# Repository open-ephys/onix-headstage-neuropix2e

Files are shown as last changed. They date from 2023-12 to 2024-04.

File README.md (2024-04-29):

# ONIX Neuropixels 2.0 Headstage

Serialized, multifunction ONIX headstage for IMEC Neuropixels-2.0 probes

**Features**
- 2x [Neuropixels 2.0](https://www.neuropixels.org/) probes per headstage
- Integrated absolute orientation tracking
- Single, 0.3 mm diameter micro-coaxial tether
- Torque-free commutation when used with an [ONIX Commutator](https://github.com/open-ephys/onix-commutator)
- 0.64 grams

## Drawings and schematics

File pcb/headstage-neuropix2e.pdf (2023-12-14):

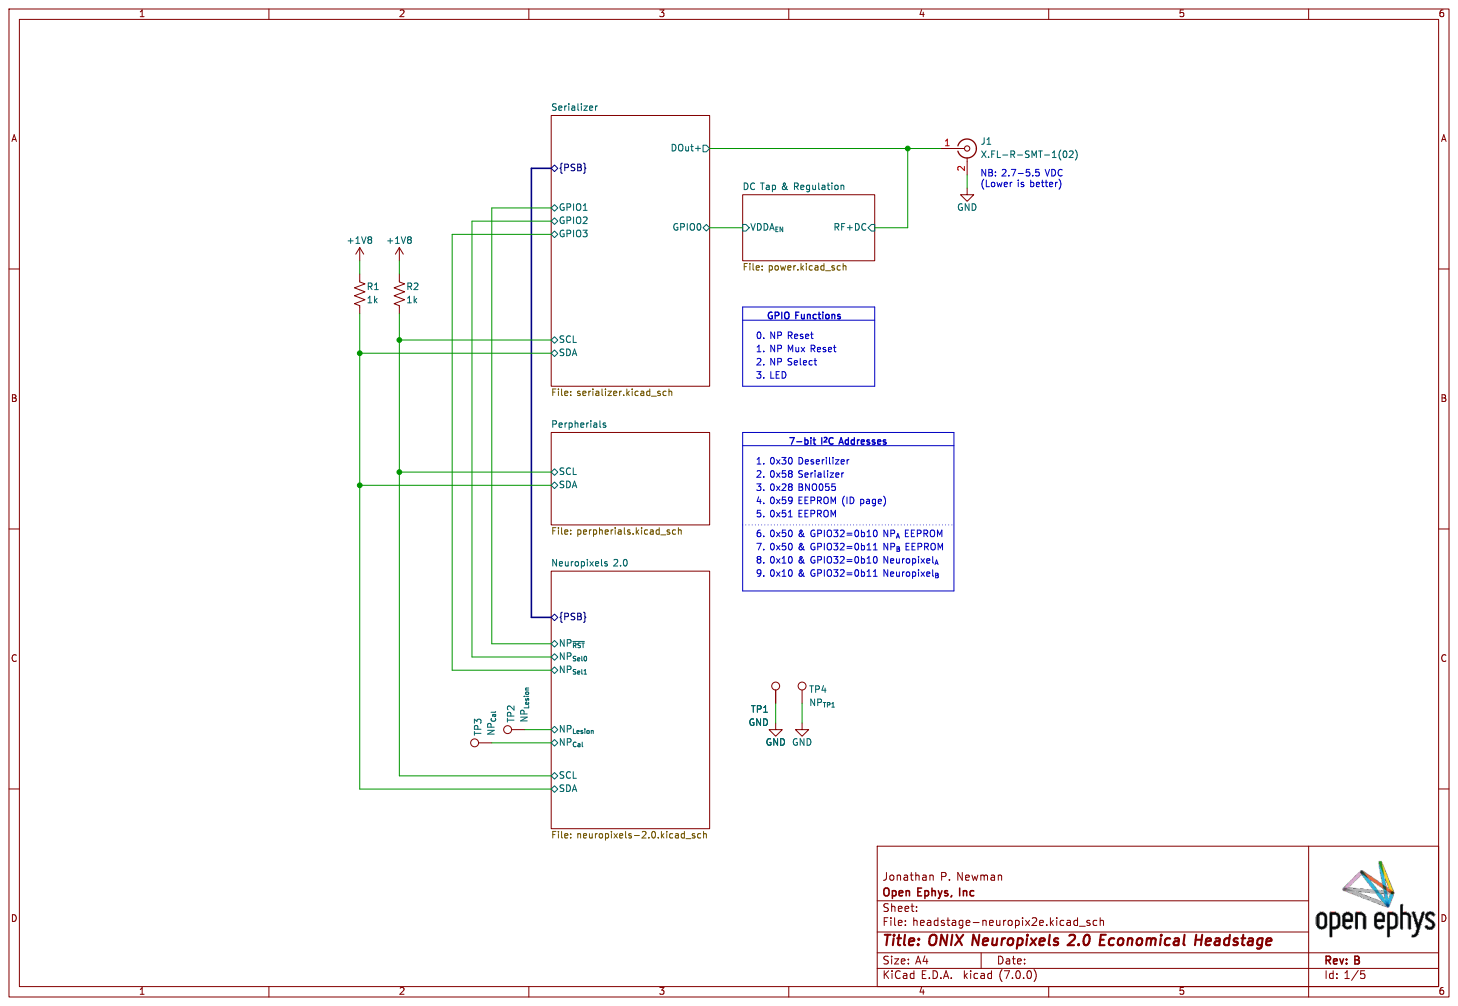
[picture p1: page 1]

{PSB} GPIO3 Serializer File: serializer.kicad_sch SDA

2. NP Select 0. NP Reset 2. 0x58 Serializer GND

1. 0x30 Deserilizer 1. NP Mux Reset GPIO Functions

Id: 1/5 Title: ONIX Neuropixels 2.0 Economical Headstage

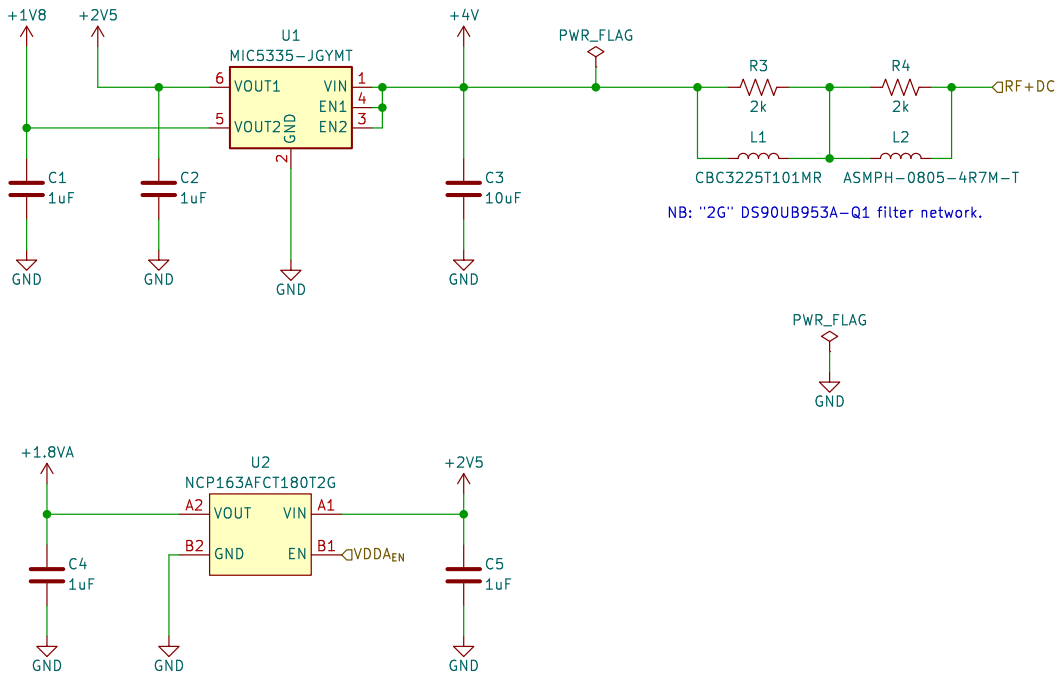
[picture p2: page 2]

Id: 5/5 Title: ONIX Neuropixels 2.0 Economical Headstage

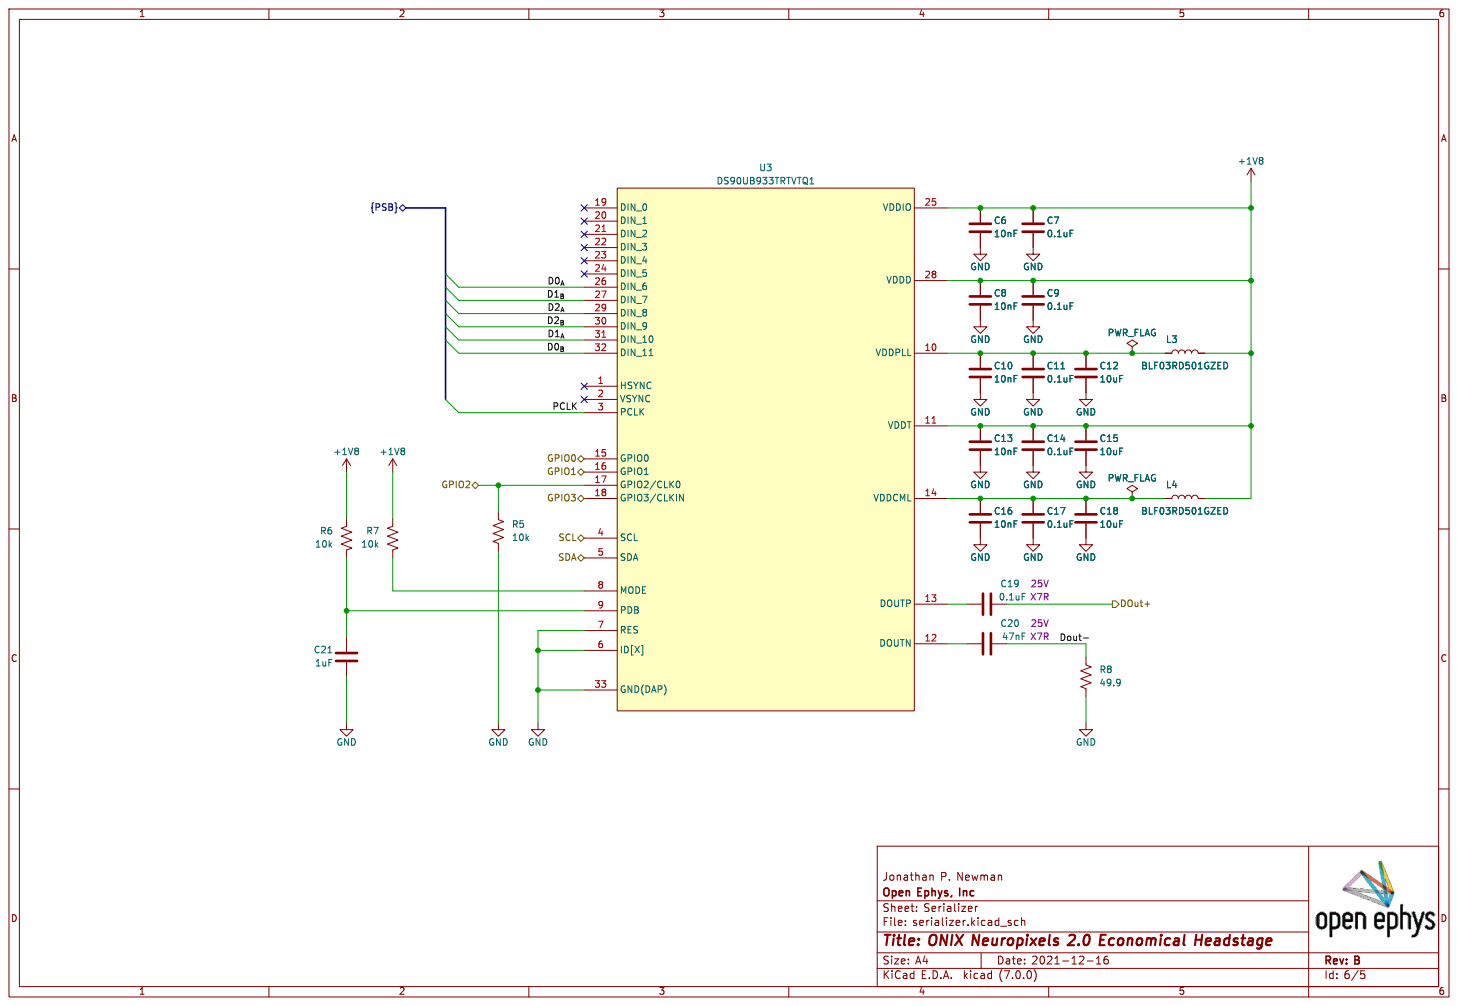
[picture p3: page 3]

Id: 6/5 Title: ONIX Neuropixels 2.0 Economical Headstage

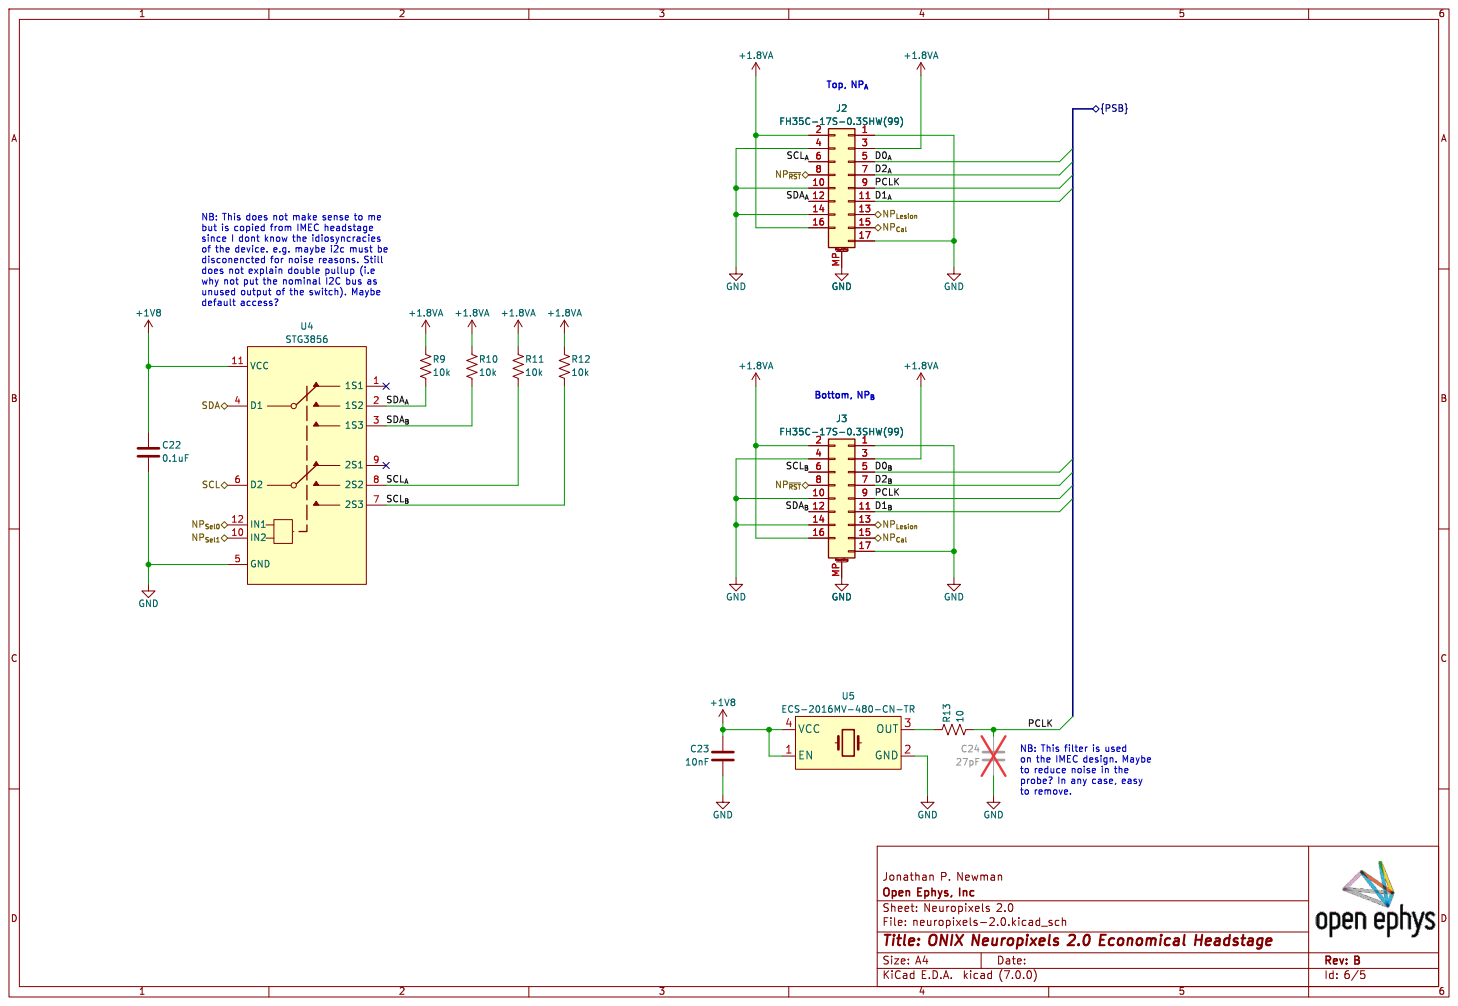
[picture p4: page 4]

Top, NP_{A} NB: This does not make sense to me

but is copied from IMEC headstage
since I dont know the idiosyncracies of the device. e.g. maybe i2c must be

why not put the nominal I2C bus as unused output of the switch). Maybe

on the IMEC design. Maybe
to reduce noise in the
probe? In any case, easy

Id: 6/5 Title: ONIX Neuropixels 2.0 Economical Headstage

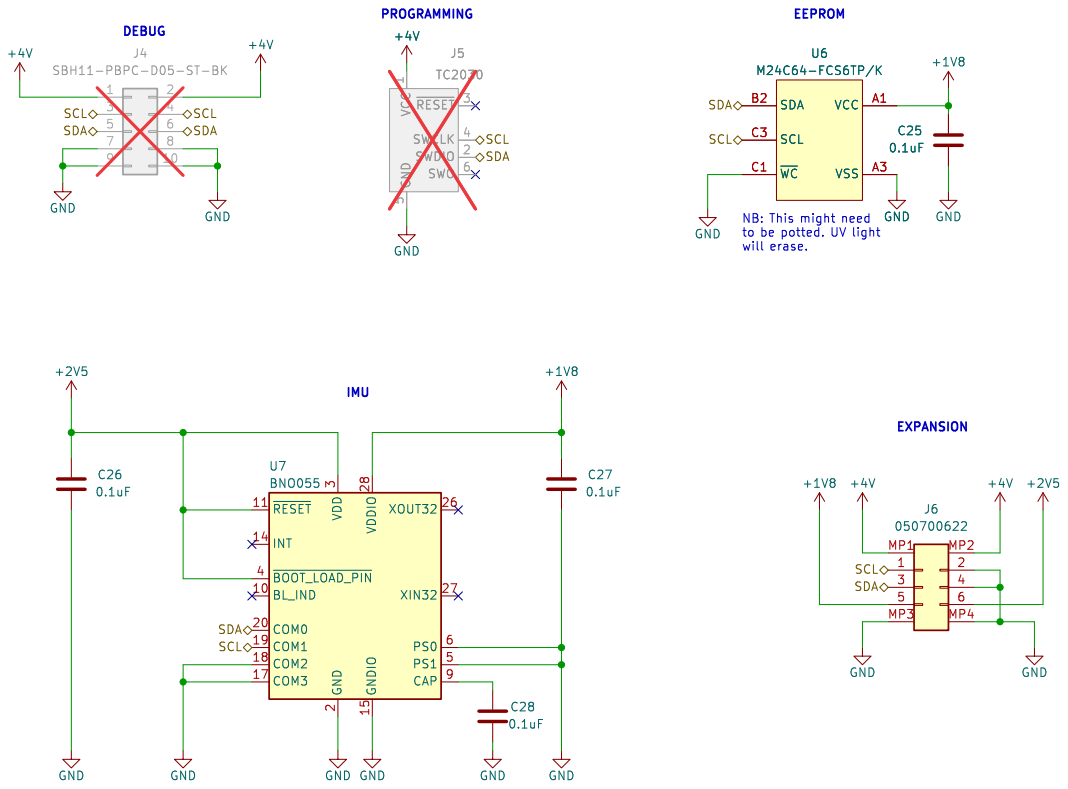
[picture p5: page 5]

1 SWDIO 2 ~{RESET}3 SWCLK 4 GND

NB: This might need
to be potted. UV light will erase.

File: perpherials.kicad_sch Sheet: Perpherials
Id: 7/5 Title: ONIX Neuropixels 2.0 Economical Headstage

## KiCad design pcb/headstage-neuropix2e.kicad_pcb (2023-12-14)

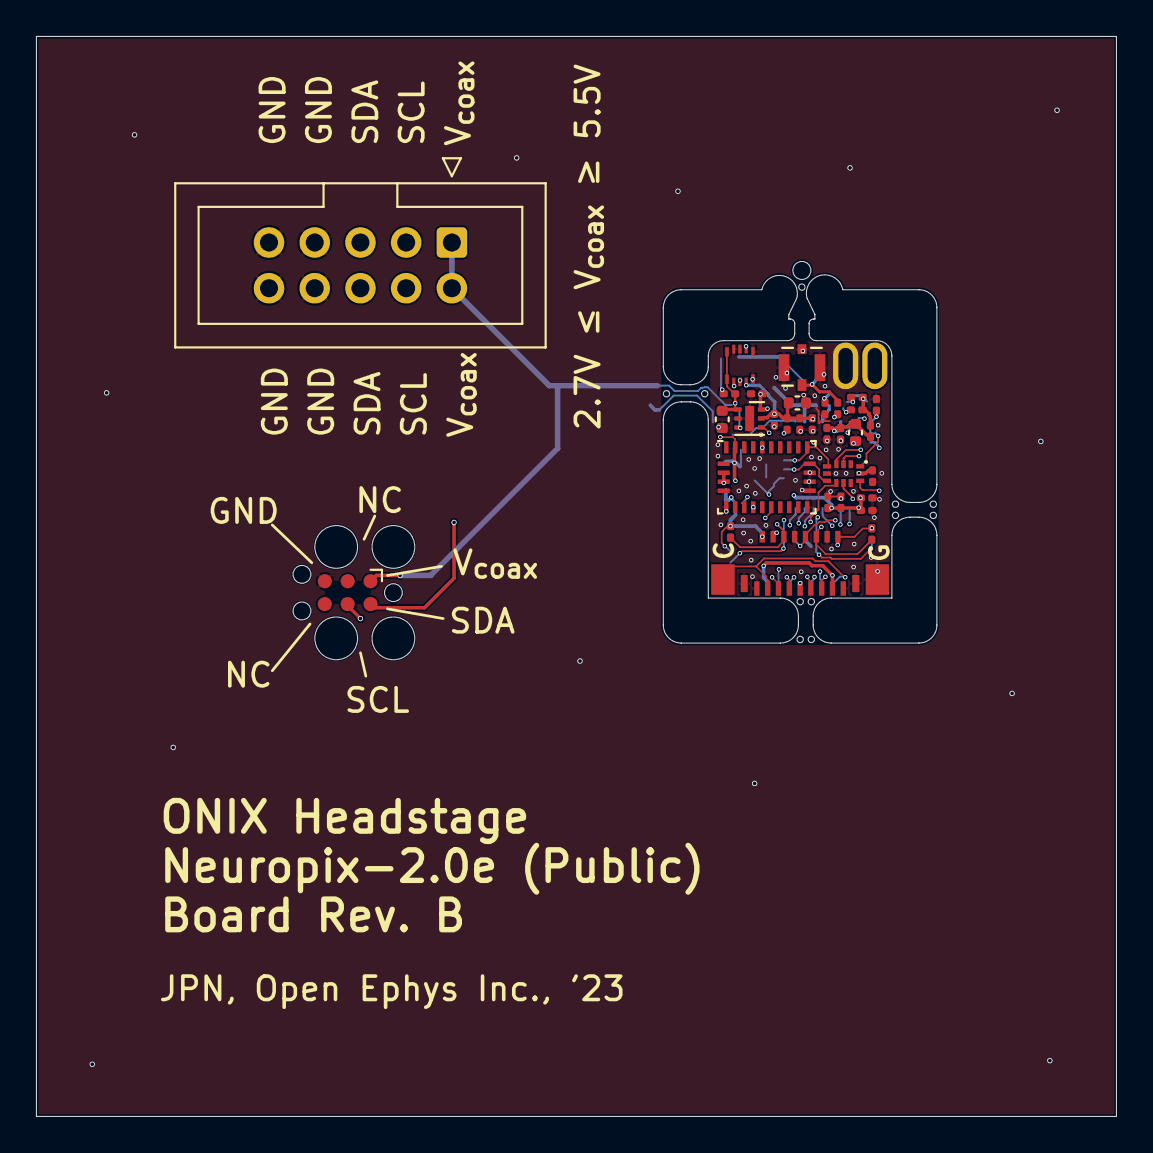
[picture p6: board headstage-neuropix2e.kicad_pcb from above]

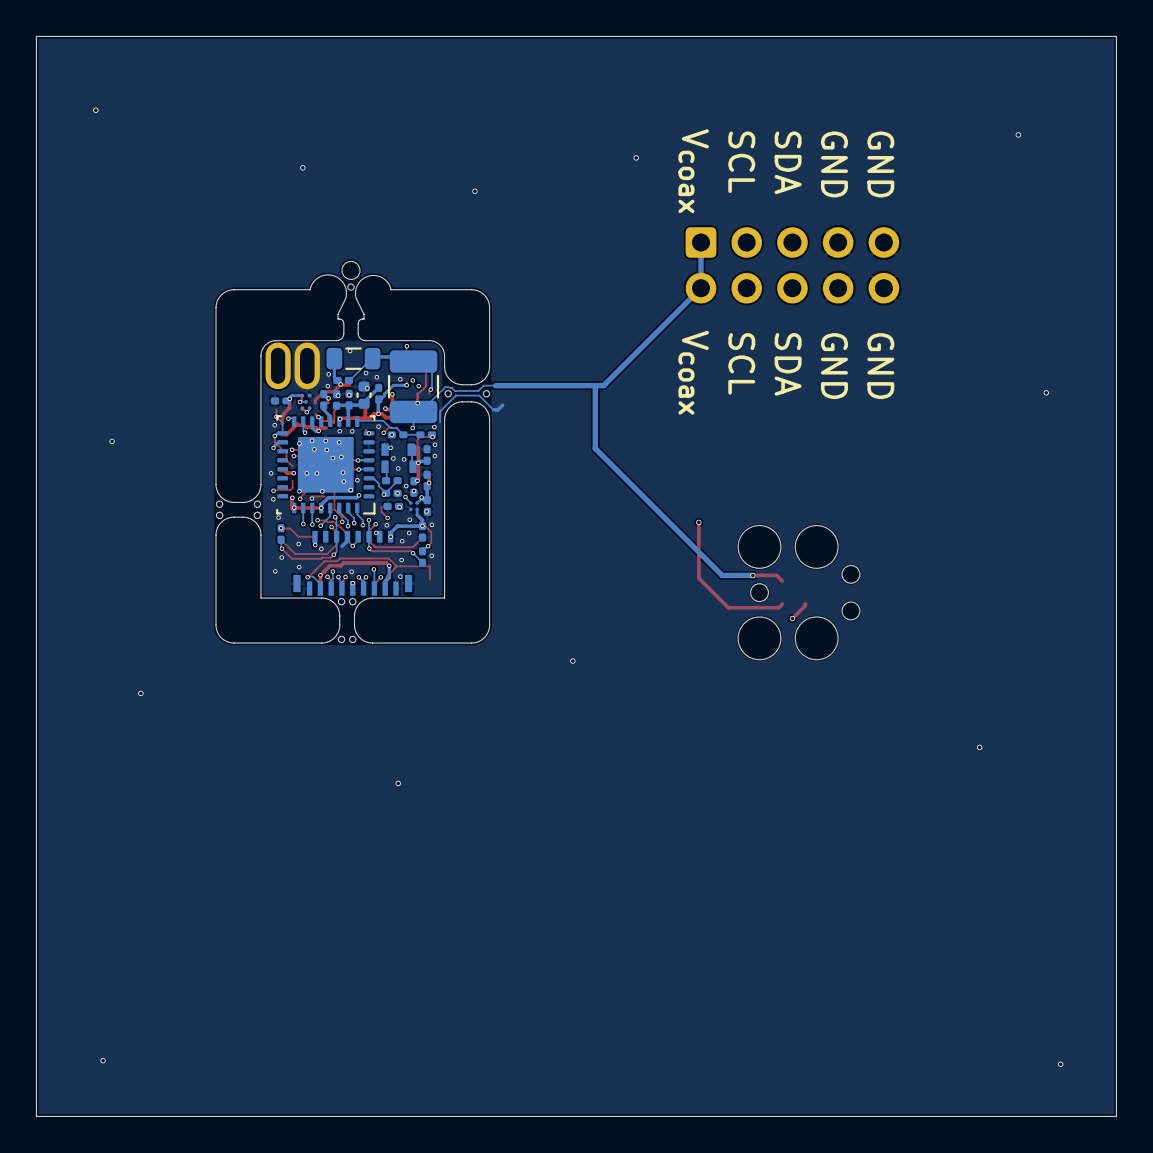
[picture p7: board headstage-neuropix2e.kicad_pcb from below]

Board: 4 copper layers, 60.0 x 60.0 mm, 62 parts (26 on the bottom side), 35 nets.

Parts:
C1, C2, C4, C5, C21: 1uF; C_0201_0603Metric
C3, C12, C15, C18: 10uF; C_0402_1005Metric
C6, C8, C10, C13, C16, C23: 10nF; C_0201_0603Metric
C7, C9, C11, C14, C17, C19, C22, C25, C26, C27, C28: 0.1uF; C_0201_0603Metric
C20: 47nF; C_0201_0603Metric
C24: 27pF; C_0201_0603Metric
J1: X.FL-R-SMT-1(02); HIROSE_X.FL-R-SMT-1
J2, J3: FH35C-17S-0.3SHW(99); HIROSE_FH35C-17S-0.3SHW(99)
J4: SBH11-PBPC-D05-ST-BK; IDC-Header_2x05_P2.54mm_Vertical
J5: TC2030; Tag-Connect_TC2030-IDC-FP_2x03_P1.27mm_Vertical
J6: 050700622; MOLEX_5050700622
L1: CBC3225T101MR; L_1210_3225Metric
L2: ASMPH-0805-4R7M-T; L_0805_2012Metric
L3, L4: BLF03RD501GZED; L_0201_0603Metric
R1, R2: 1k; R_0201_0603Metric
R3, R4: 2k; R_0201_0603Metric
R5, R6, R7, R9, R10, R11, R12: 10k; R_0201_0603Metric
R8: 49.9; R_0201_0603Metric
R13: 10; R_0201_0603Metric
TP1: GND; OE_TP-Oval-2.8x1.6mm
TP2: NP_{Lesion}; OE_TP-Oval-2.8x1.6mm
TP3: NP_{Cal}; TestPoint_Pad_1.3x1.7mm_Tight
TP4: NP_{TP1}; TestPoint_Pad_1.3x1.7mm_Tight
U1: MIC5335-JGYMT; MICROCHIP_TDFN-6-1EP_1.6x1.6mm_P0.5mm_EP0.5x1.4mm
U2: NCP163AFCT180T2G; ONSEMI_567JZ_WLCSP4-0.64x0.64
U3: DS90UB933TRTVTQ1; TI_RTV0032A
U4: STG3856; ST_QFN12L_2.2x1.4x0.55mm_P0.4mm
U5: ECS-2016MV-480-CN-TR; MICROCHIP_VFLGA4-2.0x1.6
U6: M24C64-FCS6TP/K; ST_WLCSP5-0.959x1.073
U7: BNO055; LGA-28_5.2x3.8mm_P0.5mm

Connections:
+1.8VA: C4.1, J2.2, J2.3, J2.16, J3.2, J3.3, J3.16, R9.1, R10.1, R11.1, R12.1, U2.A2 (VOUT)
+1V8: C1.1, C6.1, C7.1, C8.1, C9.1, C13.1, C14.1, C15.1, C22.1, C23.1, C25.2, C27.2, J6.5, L3.2, L4.2, R1.1, R2.1, R6.1, R7.1, U1.5 (VOUT2), U3.11 (VDDT), U3.25 (VDDIO), U3.28 (VDDD), U4.11 (VCC), U5.1 (EN), U5.4 (VCC), U6.A1 (VCC), U7.28 (VDDIO)
+2V5: C2.1, C5.1, C26.2, J6.6, U1.6 (VOUT1), U2.A1 (VIN), U7.3 (VDD), U7.4 (~BOOT_LOAD_PIN), U7.11 (~RESET)
+4V: C3.1, J4.1, J4.2, J5.1 (VCC), J6.MP1 (MountPin1), J6.MP2 (MountPin2), L1.1, R3.1, U1.1 (VIN), U1.3 (EN2), U1.4 (EN1)
/DC Tap & Regulation/RF+DC: C19.2, J1.1 (In), L2.1, R4.2
/DC Tap & Regulation/VDDA_{EN}: U2.B1 (EN), U3.15 (GPIO0)
/Neuropixels 2.0/D0_{A}: J2.5, U3.26 (DIN_6)
/Neuropixels 2.0/D0_{B}: J3.5, U3.32 (DIN_11)
/Neuropixels 2.0/D1_{A}: J2.11, U3.31 (DIN_10)
/Neuropixels 2.0/D1_{B}: J3.11, U3.27 (DIN_7)
/Neuropixels 2.0/D2_{A}: J2.7, U3.29 (DIN_8)
/Neuropixels 2.0/D2_{B}: J3.7, U3.30 (DIN_9)
/Neuropixels 2.0/NP_{Cal}: J2.15, J3.15, TP3.1
/Neuropixels 2.0/NP_{Lesion}: J2.13, J3.13, TP2.1
/Neuropixels 2.0/NP_{Sel0}: R5.1, U3.17 (GPIO2/CLK0), U4.12 (IN1)
/Neuropixels 2.0/NP_{Sel1}: U3.18 (GPIO3/CLKIN), U4.10 (IN2)
/Neuropixels 2.0/NP_{~RST}: J2.8, J3.8, U3.16 (GPIO1)
/Neuropixels 2.0/PCLK: C24.1, J2.9, J3.9, R13.2, U3.3 (PCLK)
/Neuropixels 2.0/SCL: J4.3, J4.4, J5.4 (SWCLK), J6.1, R2.2, U3.4 (SCL), U4.6 (D2), U6.C3 (SCL), U7.19 (COM1)
/Neuropixels 2.0/SCL_{A}: J2.6, R11.2, U4.8 (2S2)
/Neuropixels 2.0/SCL_{B}: J3.6, R12.2, U4.7 (2S3)
/Neuropixels 2.0/SDA: J4.5, J4.6, J5.2 (SWDIO), J6.3, R1.2, U3.5 (SDA), U4.4 (D1), U6.B2 (SDA), U7.20 (COM0)
/Neuropixels 2.0/SDA_{A}: J2.12, R9.2, U4.2 (1S2)
/Neuropixels 2.0/SDA_{B}: J3.12, R10.2, U4.3 (1S3)
/Serializer/Dout-: C20.2, R8.1
GND: C1.2, C2.2, C3.2, C4.2, C5.2, C6.2, C7.2, C8.2, C9.2, C10.2, C11.2, C12.2, C13.2, C14.2, C15.2, C16.2, C17.2, C18.2, C21.2, C22.2, C23.2, C24.2, C25.1, C26.1, C27.1, C28.1, J1.2 (Ext), J2.1, J2.4, J2.10, J2.14, J2.17, J2.MP (MountPin), J3.1, J3.4, J3.10, J3.14, J3.17, J3.MP (MountPin), J4.7, J4.8, J4.9, J4.10, J5.5 (GND), J6.2, J6.4, J6.MP3 (MountPin3), J6.MP4 (MountPin4), R5.2, R8.2, TP1.1, TP4.1, U1.2 (GND), U1.7 (GND), U2.B2 (GND), U3.6 (ID[X]), U3.7 (RES), U3.33 (GND(DAP)), U4.5 (GND), U5.2 (GND), U6.A3 (VSS), U6.C1 (~WC), U7.2 (GND), U7.5 (PS1), U7.6 (PS0), U7.15 (GNDIO), U7.16 (GNDIO), U7.17 (COM3), U7.18 (COM2), U7.25 (GNDIO)
unnamed: C10.1, C11.1, C12.1, L3.1, U3.10 (VDDPLL)
unnamed: C16.1, C17.1, C18.1, L4.1, U3.14 (VDDCML)
unnamed: L1.2, L2.2, R3.2, R4.1
unnamed: C20.1, U3.12 (DOUTN)
unnamed: C19.1, U3.13 (DOUTP)
unnamed: R7.2, U3.8 (MODE)
unnamed: C21.1, R6.2, U3.9 (PDB)
unnamed: R13.1, U5.3 (OUT)
unnamed: C28.2, U7.9 (CAP)

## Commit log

2023-02-23 Initial commit
    - Schematic: No FPGA, onboard EEPROM and BNO055 via software controlled
    I2C.
    - Rough component placement, subject to change.
    [headstage-neuropix2e.kicad_pcb, headstage-neuropix2e.kicad_sch, neuropixels-2.0.kicad_sch, perpherials.kicad_sch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]
2023-02-26 Inital routing complete
    - Addressed Aaron's review
    - Pullup on output side of analog switch to prevent floating SDA
    - Other minor changes
    [headstage-neuropix2e-B_Cu.gbr, headstage-neuropix2e-B_Mask.gbr, headstage-neuropix2e-B_Paste.gbr, headstage-neuropix2e-B_Silkscreen.gbr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]
2023-03-01 Address team comments
    - Add extra mouse-bite supports
    - Enbiggen cable strain relief spear
    - Add DNP 0.1" header for bench debug
    - Small routing changes
    - Update and complete BOM
    [headstage-neuropix2e-B_Cu.gbr, headstage-neuropix2e-B_Mask.gbr, headstage-neuropix2e-B_Paste.gbr, headstage-neuropix2e-B_Silkscreen.gbr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]
2023-03-09 Updates to design after feedback from assembler
    - Replace obsolete TE_2013496-9 ZIF connector used by IMEC with
    046844727002846+, which should fit NP 2.0 flex connectors (see design
    folder for comparison). We will see.
    - Replaced programmable MEMS oscillator with standard quartz since this
    is a common frequency.
    - Other BOM updates to account for obsolete or out of stock components
    [headstage-neuropix2e-B_Cu.gbr, headstage-neuropix2e-B_Mask.gbr, headstage-neuropix2e-B_Paste.gbr, headstage-neuropix2e-B_Silkscreen.gbr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]
2023-03-09 Forgot to update BOM in last commit
    [headstage-neuropix2e.csv, headstage-neuropix2e.kicad_pcb]
2023-09-13 Move pcb to pcb-beta directory
    - Because this board only works with Beta-test NP2.0 probes
    [headstage-neuropix2e-B_Cu.gbr, headstage-neuropix2e-B_Mask.gbr, headstage-neuropix2e-B_Paste.gbr, headstage-neuropix2e-B_Silkscreen.gbr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]
2023-09-13 Add headstage for public NP2.0 probe
    - Uses a completely different ZIF connector and bus architecture
    [headstage-neuropix2e.kicad_pcb, headstage-neuropix2e.kicad_sch, neuropixels-2.0.kicad_sch, perpherials.kicad_sch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]
2023-09-14 Revision B (Beta)
    - Neuropixels 2.0 headstage for beta-test probes
    - Updated PCB specs to match the headstage for publically avaiable
    probes (increase via size to 0.25/0.15)
    [headstage-neuropix2e-B_Cu.gbr, headstage-neuropix2e-B_Fab.gbr, headstage-neuropix2e-B_Mask.gbr, headstage-neuropix2e-B_Paste.gbr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]
2023-09-15 Rev. A of public version of headstage
    - Being fabricated for testing
    [headstage-neuropix2e-B_Cu.gbr, headstage-neuropix2e-B_Fab.gbr, headstage-neuropix2e-B_Mask.gbr, headstage-neuropix2e-B_Paste.gbr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]
2023-09-15 Fix dirll and component origin
    [headstage-neuropix2e-B_Cu.gbr, headstage-neuropix2e-B_Fab.gbr, headstage-neuropix2e-B_Mask.gbr, headstage-neuropix2e-B_Paste.gbr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]
2023-09-15 Rev. B of beta-test variant
    - This was sent for fabrication
    [headstage-neuropix2e-B_Cu.gbr, headstage-neuropix2e-B_Fab.gbr, headstage-neuropix2e-B_Mask.gbr, headstage-neuropix2e-B_Paste.gbr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]
2023-10-05 Revision A
    - This design was sent to fab
    [headstage-neuropix2e-B_Cu.gbr, headstage-neuropix2e-B_Fab.gbr, headstage-neuropix2e-B_Mask.gbr, headstage-neuropix2e-B_Paste.gbr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]
2023-11-09 Revision B
    - Fix incorrect STG3856 symbol and make corresponding changes to PCB
    - Flip bits 1 and 2 in probe interaces (fixes #1)
    - Improve silkscreen
    [headstage-neuropix2e-B_Cu.gbr, headstage-neuropix2e-B_Fab.gbr, headstage-neuropix2e-B_Mask.gbr, headstage-neuropix2e-B_Paste.gbr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]
2023-11-11 Changed debug's (J4) attribute to be excluded from the BOM.
    [perpherials.kicad_sch]
2023-11-11 Changed programming's (J5) attribute to DNP.
    [perpherials.kicad_sch]
2023-11-11 Changed expansion's (J6) attribute to be part of the BOM.
    [perpherials.kicad_sch]
2023-11-11 Added new fields (OEPS PN, MPN, and Type) to all components.
    [headstage-neuropix2e.kicad_sch, neuropixels-2.0.kicad_sch, perpherials.kicad_sch, power.kicad_sch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]
2023-11-11 Corrected MPN of J6.
    [perpherials.kicad_sch]
2023-12-07 Bring changes on schematic over to board file.
    [headstage-neuropix2e.kicad_pcb, perpherials.kicad_sch]
